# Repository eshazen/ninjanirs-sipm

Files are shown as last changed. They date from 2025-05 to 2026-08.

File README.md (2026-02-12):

# ninjanirs-sipm

Power supplies and electronics for SiPM-based optodes

Designs completed:

*  `KiCAD/lt3014-test` - test board with LT3014 voltage regulator
controlled by AD5270 digital pot, with INA201 current limiter
   * See [README](Testing/LT3014/README.md) for test details
* `KiCAD/sipm-hv-splitter` - candidate for in-system test
   * See [README](KiCAD/sipm-hv-splitter/README.md) for testing

Test logs:

* `Testing/LT3014` for the test board
* `Testing/sipm-splitter` for the splitter board

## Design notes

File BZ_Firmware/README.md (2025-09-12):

`20250827_SiPM_Test.zip`

The firmware for the purple test board is actually CircuitPython, so
it was very easy to modify. Attached, you just need to drag and drop
the .py files, and then the voltages of the 8 inputs should show up on
the serial port. If CircuitPython is not installed, I also included
the .uf2 file.

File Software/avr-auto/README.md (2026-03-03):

# avr-auto

Stand-alone bias voltage software.

* Set pull-up on PD0
* Turn off on-board LED
* Start boost converter with pot set to low voltage and output disabled
* Power up at low voltage and check voltage and current
* Power down
* Wait for low on PD0
* Power up at nominal voltage (pot=195, V=57.0V).  Check current

```
   Pot = 1023
   ADC 0 = low (10 or less)
   ADC 1 = 470  (33 volts or so)
```

LED code:
	On for 1s on power-up
	Off while waiting for start pulse
	Short blink at 1Hz during normal operation (bias on)
	fast continuous blink on error condition

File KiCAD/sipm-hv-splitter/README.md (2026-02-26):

# sipm-hv-splitter

## Description

This is a PCB intended to replace the "splitter" board, connecting
directly to a detector interface card with a very short ribbon.
It provides programmable, current-limited HV bias to 8 SiPMs along
with TIA readout of each SiPM.

The targent dimensions for the prototype are 2.5 x 1.3 inches.

The SiPM connectors are the "NIRX" standard .050" pitch 4-pin with
pinout as follows (top view of female header on this board):

| Function   | Number |   | Number | Function     |
|------------|--------|---|--------|--------------|
| V(BIAS)    | 2      |   | 1      | Signal       |
| Thermistor | 4      |   | 3      | GND (shield) |

The thermistor is optional and expected to be connected on only 1 of 8
SiPMs. 

The output connector to the readout adapter has the following pinout:

| Function | Number |   | Number | Function    |
|----------|--------|---|--------|-------------|
| V +12V   | 1      |   | 2      | V -20V      |
| GND      | 3      |   | 4      | Ch 7 signal |
| V +12V   | 5      |   | 6      | V -20V      |
| GND      | 7      |   | 8      | Ch 6 signal |
| V +12V   | 9      |   | 10     | V -20V      |
| GND      | 11     |   | 12     | Ch 6 signal |
| V +12V   | 13     |   | 14     | V -20V      |
| GND      | 15     |   | 16     | Ch 4 signal |
| V +12V   | 17     |   | 18     | V -20V      |
| GND      | 19     |   | 20     | Ch 3 signal |
| V +12V   | 21     |   | 22     | V -20V      |
| GND      | 23     |   | 24     | Ch 2 signal |
| V +12V   | 25     |   | 26     | V -20V      |
| GND      | 27     |   | 28     | Ch 1 signal |
| V +12V   | 29     |   | 30     | V -20V      |
| GND      | 31     |   | 32     | Ch 0 signal |
| COMM/RX  | 33     |   | 34     | COMM/RX     |

_NOTE:_ channel number order reversed to minimise crosstalk on the PCB.

`COMM/RX` is a logic signal (optionally containing UART prototcol
data) from the adapter card to the on-board MCU.  `COMM/TX` is an
optional half-duplex return path for bidirectional communication with
the adapter card.

## ECOs

* Cut track to SDO U5 pin 7 at chip.  Add 2.2k pull-up to 3.3V
on pin 7.
* Cut track to BOOST_ENA and wire to PD5 (pin 9) of U1.
* C39 wrong footprint on schematic/BOM (0201)

## Testing Log

### 2/26/26:

Thinking some more about the observed issues.  On the splitter the delta-v on
the LT3014 output is around 50mV, while on the test board with the MOSFET
load circuit it's more like 20mV.  50mv/57V * 1.2V = 1.1mV on the ADJ pin.
It seems not unlikely that ground bounce or capacitative coupling into the
ADJ pin could cause this.

Interesting... there is a C installed at C15 (soft start).  Try removing it.
Much better.

### 2/3/26:

Change feedback C on ch1 TIA from 1nf to 100pF.
<br>Oscillation gone!

Work plan after chat with BZ:

* Try various FB C's to make sure we're in a good range
* Change all FB C's on working board
* Test for measurable x-talk during 1.25ms pulse on neighboring channel
   * Shift in baseline
   * Change in Vbias
* Test with more SiPMs

<br>Change ch 2 FB to 470pF.  No oscillation.
<br>Change ch 1 FB back to 1000pF.  Yes oscillation (sanity check)
<br>Change ch 1-4 FB to 470pF.

### 2/2/26:

Power-up sequence:

    >p 170
	>vs 0
	>b 1

Should read 57V or so.  Note dummy load needed to avoid trip.

Testing S13360-3025PE.  3x3mm 25um pitch.  Vover = 5V, VBR 53+/-5
<br>Confirm that VBR is about 53.

   S13360-3025PE (gain 7e5)
   pot = 195.  V is 56V, 170uA+/-50uA
   100Hz pulse 100us wide 3.2V into red LED
   Output about 420mV.
   
Printing another box for a 2nd SiPM.

   S13360-3050PE (gain 1.7e6)
   Output about 3.95V
   
Gain should be about 2.5X higher.

__Oscillation:__ See 50MHz sine wave ~ 20mV pk-pk output of amp.
<br>With only open NIRX cable (60cm) we see a square-ish wave almost 100mV pk-pk.

The amp has a low-pass filter with ~10kHz cutoff.
<br>Try 100pF in parallel with the 1nF feedback cap.  If anything, worse.

### 1/22/26:

See below 8/7/25 for power hookups

Test board `OUT0` is pin 4 of ribbon, so SIG_0 which comes from pins 29-32 of Optodes header

Boost converter producing 73V but output always tripped.  Need dummy load?
<br>Make a optode cable with 100k.  Now it works!

The current readback seems wrong, though.  57/100k = 560uA
<br>The readout says 72.6uA

ADC is reading 31.  Sense resistor is 3.00 ohms.  So the raw current signal
should be 1.7mV across R9.  For the INA201 the gain is supposedly 50V/V
so 84mV for 560uA.  The expected ADC reading would be 26.  Observe 31-35
using raw `a 0` so maybe not so bad?

In `sipm_io.h` constant `NA_PER_ADC` is 2200.  Hmm.
Change to 20687.

### 9/30/25:

Testing board#2

* Power-up and flash OK.
* Boost output 73V
* VR range 31.2-60.8

* Change R17 to 2.7M to increase max voltage to 67V

Now the VR goes up to 65.2.

The current readback is jumping around from 8-20uA though.

Re-flash board#1 with avr-debug

Current readback similarly jumps around

### 9/17/25:

(all below board#1)

Finally have correct (hope) ribbon between test board and adapter.
Going to install firmware on the purple test board.

Currently it has:

```
hazen@hazen-botlab CIRCUITPY $ ls -l
total 6
-rw-r--r-- 1 hazen hazen  103 Dec 31  2019 boot_out.txt
-rw-r--r-- 1 hazen hazen 1608 Dec 18  2022 code.py
-rw-r--r-- 1 hazen hazen 2671 Dec 19  2022 DetAdapterTB.py
drwxr-xr-x 2 hazen hazen  512 Dec 31  2019 lib
```

(lib is empty).  Copying the following from BZ's ZIP:

```
-rw-rw-rw- 1 hazen hazen     889 Aug 28 00:51 code.py
-rw-rw-rw- 1 hazen hazen    8512 Aug 28 00:47 NN22DetectorAdapterTestBoard.py
-rw-rw-rw- 1 hazen hazen    3982 Oct 17  2024 TestFunctions.py
```

It works!  SiPM output voltage reported by python on the test board
varies with LED current.

### 9/12/25:

Working towards readout with BZ's red and purple boards.

TODO:

* Install R63, remove R62 on red board.  This disables the on-board LED and repurposes `A_COMM` as an
enable for the HV.  _Done_ (100 ohms for R63)
* Make firmware which powers up the HV and displays status
on the HV board LED.

### 9/11/25:

* Change R13 to 180k to up boost output to 75V.
* Change R17 to 2.7M to increase max voltage to 67V

Confirm with VOM we get 66.5V max output or so.

### 8/27/25:

Looking to use [test board](https://github.com/eshazen/ninjanirs-optode/tree/main/KiCAD/test-board) as a breakout.

```
  +6.5V  -  use for +12V power
  GND    -  ground
  -20V   -  use for -20V for TIA negative power
```

Solder wires to J1 pins 33 (comm TX) and 34 (comm RX).

### 8/20/25:

Load resistor of 66k on outputs.  Script `ramp_plot.py` makes
a nice set of V, I curvs vs DAC setting.

Ripple with scope probe ~ 20mV pk-pk.  100MHz always present,
20Hz (!) only when boost converter on.

Install parts for detector 0:

```
   R44, C47  (1k, 0.1uF) bias filter
   C23, C31 (0.1uF) bypass
   R28 (15k, TI)
   U13 (opa)
   R36 (15 ohms) output
   C39 (1n) feedback
```

### 8/4/25:

Issues with oscillation on output; seems like the LT3014.
Change C11 and C12 to 1uF 100V (vs 0.1uF).  Seems better.
Still some issues with startup.

Change R3 from 140k to 75k (double the overcurrent).
Now all seems good except for some ripple at max output.
Change R13 from 180k to 160k to up boost output to 65V.

All good so far.

### 7/29/25:

Add 2.2k pull-up on Digi Pot SDO.  It works!
<br>Move `BOOST_ENA` to PD5

Install U4, R17, R20 and C11, C12 as 0.1uF 100V.

### 7/28/25:

Started a new board, installed MCU and digi pot.

Found that ISP is unreliable here too.  Cut "SDO" track from digipot.
Now it seems to work reliably.  But Digi pot doesn't work.

Notice that the data sheet says that a pull-up is *required* on SDO
even if not used.

### 7/24/25:

Found a "feature" of the AVR SPI bus:  The pin called nSS (PB2)
must be driven high for the SPI bus to work.  We're using this
for BOOST_ENA so this is a bit of a problem.

More seriously, the ISP interface on the AVR seems to be dead.
This could be because we were using the ISP in 5V mode :(
<br>One can set 3.3V (host power) mode by removing the little yellow jumper
on the USBTinyISP.

May need to solder up a new board :( :(
<br>Start on board#2.  Install only 3.3V digital and MCU.
Programs fine.  Stopping for the weekend.

### 7/23/25:

Soldered 3.3V regulators, MCU and boost converter parts.
Soldered temporary FTDI serial thing on R1 site.

Boost converter works!  Outputting 61.3V, drawing 69mA on 12V.
Controlled as expected by `BOOST_ENA` output from MCU.

Install Digi pot.  Doesn't work :(  <br>
Verified SCK, MOSI, nSYNC all look OK. <br>
Nothing comes out MISO, POT stuck at 50%. <br>

Giving up for today

## Revision log

### 7/7/25:
Final checks

* Add LC filter on AVCC on MCU
* Add filter C on AREF
   * working on layout changes

### 7/3/25:  
First complete draft, posted to Basecamp

### Edits due from BZ on 7/1/25:

* Mis-wired RC filter on TIA input; should be on each SiPM bias line.
<br>_NOTE:_ the RC filter should be moved to the heirarchial block for
each channel for common layout? *DONE*
* Swap UART TX/RX *DONE*
* Use same symbol for all caps C2, C3 etc *DONE*
* Add filter on `THERM` *DONE*

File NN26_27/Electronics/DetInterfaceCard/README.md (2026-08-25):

## Detector card V03

Two variants:

| Designator | NN24-26        | NN27  | Notes                             |
|------------|----------------|-------|-----------------------------------|
| R71        | DNP            | 0 Ohm | New component / designator        |
| LF1        | BLM18AG601SN1D | DNP   | Ferrite 600 Ohm @ 100 MHz, 500 mA |

Additional components could be DNP’d in NN27 if desired, such as U13 and C104.

**2026-08-24**

Trying to order.  Two problem parts:

C89 etc.  10uF X5R 0402

D1-D2  SBR1A20T5-7  1A fast response diode.  A problem.

Possible sub:  SBR1U40LP-7 in DFN package about the same size.
Make this change in `develop` (KiCAD conversion).  Layout done.

BOM is a problem... the KiCAD import doesnt include MPN.

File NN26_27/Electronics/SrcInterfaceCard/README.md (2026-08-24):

# Source adapter V02

Two different possible assemblies here:

* NN22_VCCS_SrcAdapter02_s00_Gerber.zip -- Standard version
* NN22_VCCS_SrcAdapter02_s00_HiPower.zip -- High power version

The high power version has several BOM changes:

```
 Designator    NN24              NN26         Notes
 R9            10 Ohm            1 Ohm        Change in damping network
 R13           DNP               2.2 Ohm      Change in damping network
 C12           DNP               0.22 uF      Change in damping network
 R8            8.2 Ohm           1.5 Ohm      Current shunt for higher amps
 R30           28 kOhm           59 kOhm      Increase LED drive voltage for series cfg
 F1            0ZCH0035FF2G      0ZCH0110AF2E Increase fuse amps
 R2            10 kOhm           12 kOhm      Tune max amps slightly lower
```

Also the bottom silkscreen label has been changed to add the date 2026
and the notation "HIGH POWER".

There is an updated BOM downloaded from MacroFab.

As of today (8/6/26) the MacroFab design NN22_VCCS_SrcAdapter02
version 2 is the high power version.  Version 1 is the std one.

**2026-08-24** Ordered 20 pcs of the HP source adapter on Macrofab (#jr15eh3)

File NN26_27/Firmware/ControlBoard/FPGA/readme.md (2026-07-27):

For low-level Matlab functions or the old Matlab based NinjaGUI, which use the **USB** connection, use:  
`NN22Control00g5-ExtFifo-VCCS-VBoost-7000HC`

For use with **NinjaWeb**, running on the on-board Raspberry Pi Zero, which uses the **SPI** connection, use:  
`NN22Control00j-SPIctrl-Status-7000HC`

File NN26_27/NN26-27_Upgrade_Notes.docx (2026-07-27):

# NinjaNIRS 2026/27 Upgrade Notes

As of July 27, 2026

Github repo for all design files that have changed compared to the public version on OpenfNIRS: https://github.com/eshazen/ninjanirs-sipm/tree/main/NN26_27/

# NinjaNIRS 2026

NN26 is a planned upgrade of the two NN24 whole-head, high-density systems at BU with high-power source optodes, as designed and tested for the UG3 grant milestones.

## Source Optodes

NIRx is in the process of manufacturing high-power source optodes for us. Assembly instructions as well as the PCB design files for the small board inside each optode are in the Github repo.

## Source Splitter Boards

In testing we have used the NIRx source splitter PCBs and didn’t see any issues. It might still be worth checking the current handling capacities of the PCB traces.

The traces on Eric’s source splitter were designed with the higher currents in mind, but we have only manufactured a few of them.

## Source Interface Cards

The NN24 VCCS Source Interface cards from NN24 can also be used for NN26, however several components need to be changed, so it is probably more economical to order new sets of PCBs. Obviously regular NIRx source optodes should not be connected to these modified boards as the LEDs could easily be overdriven!

Here are the components that need to be changed:

Designator | NN24 | NN26 | Notes
R9 | 10 Ohm | 1 Ohm | Change in damping network
R13 | DNP | 2.2 Ohm | Change in damping network
C12 | DNP | 0.22 uF | Change in damping network
R8 | 8.2 Ohm | 1.5 Ohm | Current shunt for higher amps
R30 | 28 kOhm | 59 kOhm | Increase LED drive voltage for series cfg
F1 | 0ZCH0035FF2G | 0ZCH0110AF2E | Increase fuse amps
R2 | 10 kOhm | 12 kOhm | Tune max amps slightly lower

## Backplane

The NN24 backplane should be fine. Any backplane with “VCCS” in the designator should be compatible. Only the oldest (v1) backplanes are not compatible as they were designed for the first version source cards without current source.

## Control Card

Currently one NN24 system has a v2 control card, the other one has a v3 control card. Both are compatible with the high power optodes, though it would make sense to upgrade the system with the v2 card to v3 when working on it. V3 supports the voltage/current monitoring Sreekanth added to the NinjaWeb.

## System Case

The current case should be fine.

## Firmware / NinjaWeb GUI

It would be highly advisable to implement some additional safety features to prevent the average optical power of a single optode to exceed ANSI limits. This could currently happen if someone e.g. loads a wrong probe file for much smaller probe so that now the duty cycle of a single optode is much higher.
This safety could e.g. be implemented in the source card firmware, running separately on the second core of the MCU which is currently not used. Or a simpler version could be implemented in NinjaWEB, though this would not catch e.g. as stall in the FPGA.

In NinjaWEB, make sure that in NN24SystemClass.py the following is set:

self.v_src_boost = True

This will increase the source card supply voltage from 5.2V to 9.7V.

A similar setting is in the Matlab initStat() function: stat.v_src_boost = true;

# NinjaNIRS 2027

NN27 is a further planned upgrade of the two whole-head, high-density systems at BU with SiPM based high-detectivity optodes, as designed and tested for the UG3 grant milestones.

## Detector Optodes

Detector optodes can be manufactured by NIRx in exactly the same way as source optodes. PCB design files are in the Github repo.

## Detector Splitter Boards

Eric has designed splitter boards that contain the necessary bias voltage generator. A set of these will have to be ordered, maybe including minor revisions.

Protection of the user from the ~60V bias voltage should also be considered. Potting or conformal coating could be explored.

## Detector Interface Cards

The detector interface cards stay largely the same. The only change is to route 12V directly to the splitter board to power the bias generator. This can either be done by manually soldering a jumper wire on a current board, bypassing U13, or by manufacturing a new set of v3 cards with the following changes:

Designator | NN24-26 | NN27 | Notes
R71 | DNP | 0 Ohm | New component / designator
LF1 | BLM18AG601SN1D | DNP | Ferrite 600 Ohm @ 100 MHz, 500 mA

Additional components could be DNP’d in NN27 if desired, such as U13 and C104.

## Backplane

The existing backplanes are compatible.

## Control Card

Similar to the detector cards, 12V must be routed to the backplane to ultimately power the bias generators. The v3 Control Cards already have provisions for this. V1 and V2 cards are not compatible.

Here are the necessary changes on the v3 control card:

On the front side of the card, bridge pads 3 and 5 of connector footprint J901.

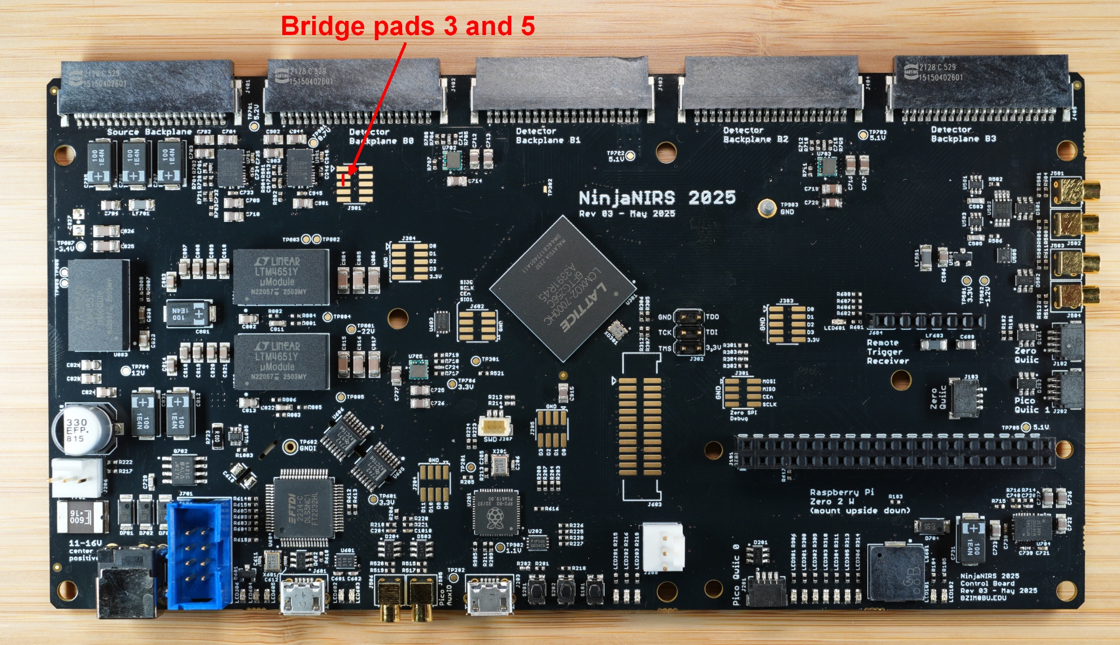
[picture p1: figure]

On the back side of the card, move the 0 Ohm resistor from R401 to R402, from R403 to R404, from R405 to R406, and from R407 to R408.

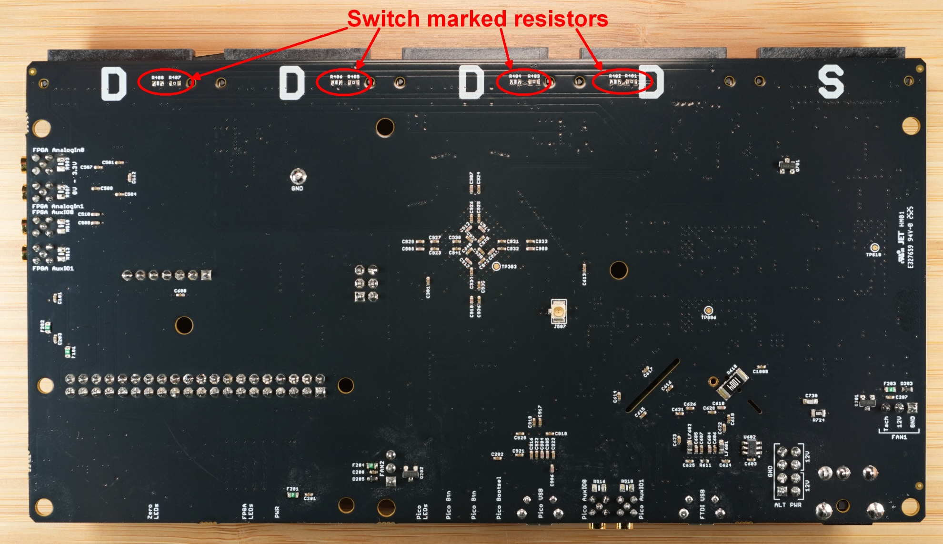
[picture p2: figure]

## System Case

The system case must be redesigned / enlarged to accommodate the larger detector splitter boards, and possibly to protect the user from the bias voltage.

## Firmware / NinjaWeb GUI

As a starting point, no firmware needs to be changed.

However, if control of bias voltage is necessary, it might be desirable to coordinate changes with the larger system, so communication between the splitter board and detector interface board has to be implemented, and then enable communication of this new data to NinjaWeb will also require changes to the FPGA firmware.

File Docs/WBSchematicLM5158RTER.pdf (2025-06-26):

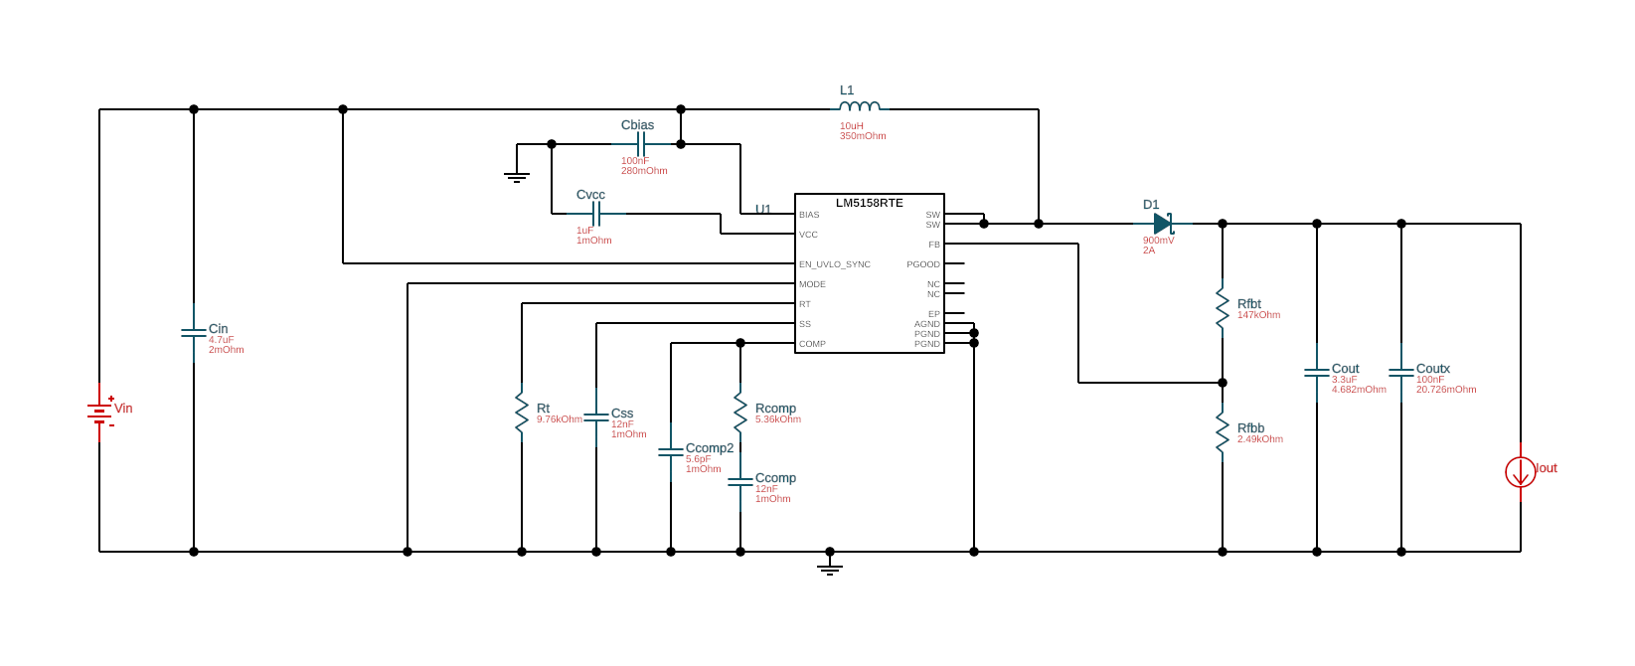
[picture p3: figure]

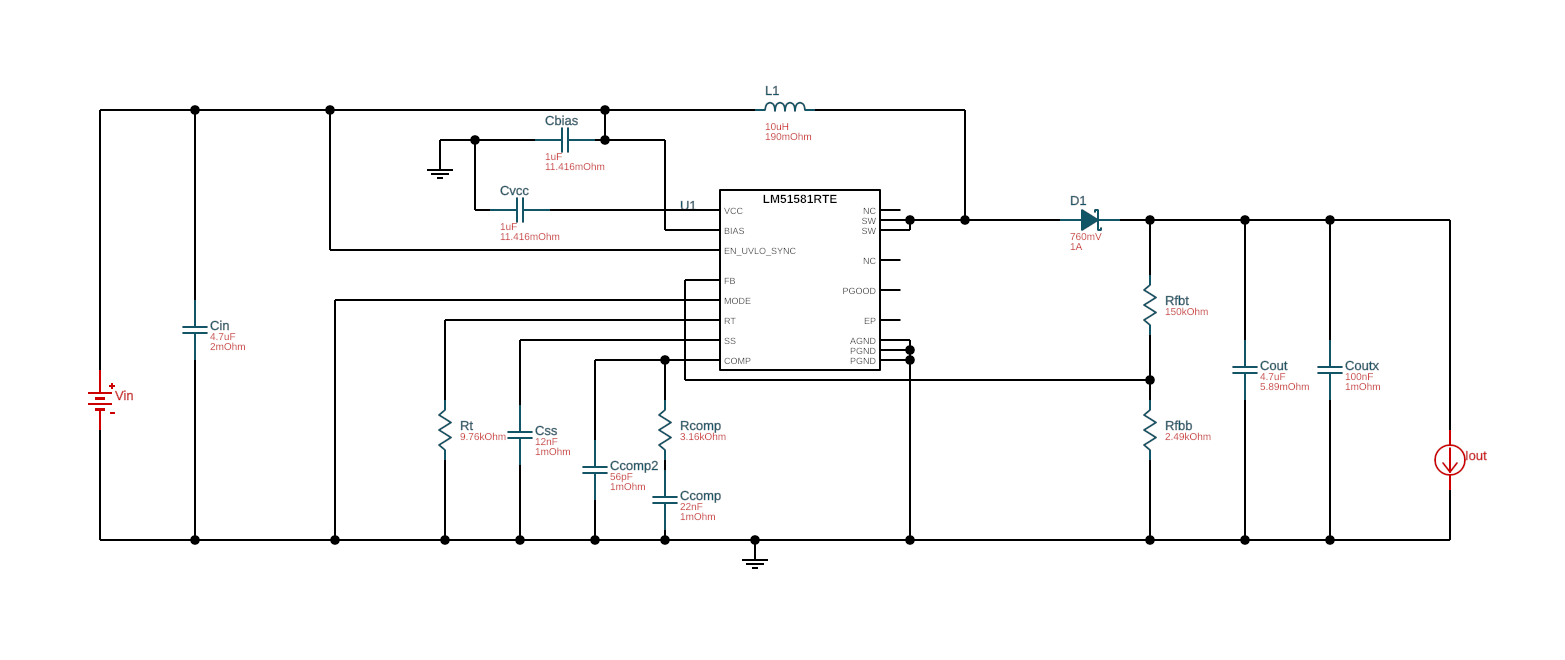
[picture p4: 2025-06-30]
Docs/WBSchematicLM51581RTER.png

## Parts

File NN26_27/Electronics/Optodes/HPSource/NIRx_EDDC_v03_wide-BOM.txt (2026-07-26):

LED1, LED2: Marubeni EDCC760D-1100
LED3, LED4: Marubeni EDCC850D-1100

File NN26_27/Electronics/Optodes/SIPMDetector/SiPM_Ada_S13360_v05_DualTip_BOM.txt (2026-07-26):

PD1, PD2: Hamamatsu S13360-3050PE
R1: NTCG163JF103FT1
TP1, TP2, TP3, TP4: DNP (wire solder pads)

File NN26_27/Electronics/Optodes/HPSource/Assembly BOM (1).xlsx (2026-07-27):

Type | No. | Description | Quantity per | Unit of Measure Code | Position
Item | ACLIP4 | POD Clip - 4 | 2 | PCS
Item | ACLIP8 | POD Clip - 8 | 1 | PCS
Item | NC000625 | Active SR2/DT2 optode cable Rev.04 (0.7M) | 8 | PCS
Item | NC000116 | Shrink Tube 1.6/0.5, 3:1, transp. (Optode Cable) | 0.152 | M
Item | NC000137 | Detector housing; double tip (DUAL CHIP SENSOR TIP) | 8 | PCS
Item | NC000192 | Optode cap blue | 8 | PCS
Item | NC000455 | Detector Box with cover for NSP2 (machined) | 1 | PCS
Item | NC000447 | SR2-POD-PCB | 1 | PCS

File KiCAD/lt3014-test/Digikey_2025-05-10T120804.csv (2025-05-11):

Index | Quantity | Part Number | Manufacturer Part Number | Description | Customer Reference | Available | Backorder | Unit Price | Extended Price USD
1 | 2 | 2648-SC0917-ND | SC0917 | RASPBERRY PI PICO H RP2040 | A1 | 2 | 0 | 5.00000 | 10.00
2 | 10 | 399-C0603C103M4REC7411CT-ND | C0603C103M4REC7411 | CAP CER 0603 10NF 16V X7R 20% | C6,C9 | 10 | 0 | 0.05400 | 0.54
3 | 10 | 3147-B19Y1USD-20C000113U1930CT-ND | B19Y1USD-20C000113U1930 | LED RED CLEAR 0603 SMD | D1,D2,D3,D4 | 10 | 0 | 0.09900 | 0.99
4 | 10 | SAM10844-ND | TSW-102-07-F-S | CONN HEADER VERT 2POS 2.54MM | J1,J2,J3 | 10 | 0 | 0.11000 | 1.10
5 | 10 | 609-3257-ND | 68000-208HLF | CONN HEADER VERT 8POS 2.54MM | J4 | 10 | 0 | 0.44900 | 4.49
6 | 10 | 609-3255-ND | 68000-204HLF | CONN HEADER VERT 4POS 2.54MM | J5 | 10 | 0 | 0.27000 | 2.70
7 | 10 | BSS138CT-ND | BSS138 | MOSFET N-CH 50V 220MA SOT23-3 | Q3,Q4,Q5 | 10 | 0 | 0.16100 | 1.61
8 | 10 | RMCF0603FT3R00CT-ND | RMCF0603FT3R00 | RES 3 OHM 1% 1/10W 0603 | R1 | 10 | 0 | 0.02400 | 0.24
9 | 10 | RMCF0603FT2M49CT-ND | RMCF0603FT2M49 | RES 2.49M OHM 1% 1/10W 0603 | R2 | 10 | 0 | 0.02400 | 0.24
10 | 10 | 13-RT0603BRD0750KLCT-ND | RT0603BRD0750KL | RES 50K OHM 0.1% 1/10W 0603 | R3 | 10 | 0 | 0.10800 | 1.08
11 | 10 | YAG1676CT-ND | RT0603BRD074K7L | RES SMD 4.7K OHM 0.1% 1/10W 0603 | R4 | 10 | 0 | 0.10000 | 1.00
12 | 20 | YAG1570CT-ND | RT0603BRD071K5L | RES SMD 1.5K OHM 0.1% 1/10W 0603 | R6,R8,R17,R18 | 20 | 0 | 0.10100 | 2.02
13 | 3 | LT3014ES5#TRPBFCT-ND | LT3014ES5#TRPBF | IC REG LIN POS ADJ 20MA TSOT23-5 | U1 | 3 | 0 | 6.07000 | 18.21
14 | 3 | 296-INA201AIDRCT-ND | INA201AIDR | IC CURRENT MONITOR 3.5% 8SOIC | U3 | 3 | 0 | 3.74000 | 11.22
15 | 3 | 505-AD5270BRMZ-50-ND | AD5270BRMZ-50 | IC DGT RHE 50KOHM 1024TAP 10MSOP | U4 | 3 | 0 | 6.75000 | 20.25
16 | 10 | 1276-1946-1-ND | CL10B105KP8NNNC | CAP CER 1UF 10V X7R 0603 | C4,C5,C7 | 10 | 0 | 0.00500 | 0.05
17 | 10 | 311-10.0KHRCT-ND | RC0603FR-0710KL | RES 10K OHM 1% 1/10W 0603 | R5,R10,R15 | 10 | 0 | 0.00900 | 0.09
18 | 10 | 311-100KHRCT-ND | RC0603FR-07100KL | RES 100K OHM 1% 1/10W 0603 | R7,R16 | 10 | 0 | 0.00900 | 0.09
19 | 10 | 311-100KHRCT-ND | RC0603FR-07100KL | RES 100K OHM 1% 1/10W 0603 | R9 | 10 | 0 | 0.00900 | 0.09
20 | 10 | 311-210KHRCT-ND | RC0603FR-07210KL | RES 210K OHM 1% 1/10W 0603 | R11 | 10 | 0 | 0.00900 | 0.09
21 | 10 | 311-140KHRCT-ND | RC0603FR-07140KL | RES 140K OHM 1% 1/10W 0603 | R12 | 10 | 0 | 0.00800 | 0.08
22 | 10 | 311-0.0GRCT-ND | RC0603JR-070RL | RES 0 OHM JUMPER 1/10W 0603 | R13,R14 | 10 | 0 | 0.01000 | 0.10

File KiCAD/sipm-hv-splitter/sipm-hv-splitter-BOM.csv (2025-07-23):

Build Qty: | 3
Reference | Qty | Value | MfgNo | CatNo | OrderQty
C1 | 1 | 4.7uF | CL10A475KO8NNNC | 1276-1784-1-ND | 3
C2,C3,C6,C48,C50,C52,C53 | 7 | 1.0uF | CL10B105KO8NNNC | 1276-1019-1-ND | 21
C4,C16,C17,C18,C19,C20,C21,C22,C23,C24,C25,C26,C27,C28,C29,C30,C31,C40,C41,C42,C43,C44,C45,C46,C47,C54,C55 | 27 | 0.1uF | CC0603KRX7R7BB104 | 311-1088-1-ND | 81
C5,C13 | 2 | 10nF | 06035C103MAZ2A | 478-KGF15AR71H103MTCT-ND | 6
C7 | 1 | 22nF | 0603B223K160CT | 1292-1415-1-ND | 3
C8 | 1 | 56pF | 600S560JT250XT4K | 478-600S560JT250XT4KCT-ND | 3
C9 | 1 | 4.7uF 100V | GRM31CC72A475KE11L | 490-18620-1-ND | 3
C10 | 1 | 0.1uF 100V | CL10B104KC8NNNC | 1276-6807-1-ND | 3
C11,C12,C14 | 3 | 1.0uF 100V | GRM188D72A105ME01W | 490-GRM188D72A105ME01WCT-ND | 9
C32,C33,C34,C35,C36,C37,C38,C39 | 8 | 1nF | CL03B102KOSVPNC | 1276-CL03B102KOSVPNCCT-ND | 24
C49,C51 | 2 | 2.2uF | TMK107ABJ225KA-T | 587-2909-1-ND | 6
D1 | 1 | MBR1H100SFT3G | MBR1H100SFT3G | MBR1H100SFT3GOSCT-ND | 3
D2,D3 | 2 | LED | B19Y1USD-20C000113U1930 | 3147-B19Y1USD-20C000113U1930CT-ND | 6
J1 | 1 | Conn_02x18_Odd_Even | SFMC-118-02-S-D | SFMC-118-02-S-D-ND | 3
J2 | 1 | Conn_02x17_Odd_Even | SHF-117-01-L-D-SM | SAM9921-ND | 3
J3 | 1 | ISP | BC065-06-A-L-D | 2073-BC065-06-A-L-D-ND | 3
L1 | 1 | 10uH | 744025100 | 732-2617-1-ND | 3
L2 | 1 | 10uH | MLZ1608N100LT000 | 445-6755-1-ND | 3
Q1,Q2,Q3 | 3 | BSS138 | BSS138 | BSS138CT-ND | 9
R1,R37,R38,R39,R40,R41,R42,R43,R44 | 9 | 1k | RMCF0603FT1K00 | RMCF0603FT1K00CT-ND | 27
R2 | 1 | 210k | RC0603FR-07210KL | 311-210KHRCT-ND | 3
R3 | 1 | 140k | RC0603FR-07140KL | 311-140KHRCT-ND | 3
R4 | 1 | 100k | RC0603FR-07100KL | 311-100KHRCT-ND | 3
R5,R6,R16,R46 | 4 | 10.0k | CRCW0603100KFKEA,RC0603FR-0710KL | 311-10.0KHRCT-ND | 12
R7 | 1 | 100k | CRCW0603100KFKEA | 541-100KHCT-ND | 3
R8,R10 | 2 | 100 | ERJ-3EKF1000V | P100HCT-ND | 6
R9 | 1 | 3.00 1% | MFCR1206F3R00QHR | 4506-MFCR1206F3R00QHRCT-ND | 3
R11 | 1 | 4.7k | RT0603BRD074K7L | YAG1676CT-ND | 3
R12 | 1 | 3.16k | CRCW06033K16FKEAC | 541-5389-1-ND | 3
R13 | 1 | 150k | ERJ-3EKF1503V | P150KHCT-ND | 3
R14 | 1 | 2.49k | CRCW06032K49FKEAC | 541-4044-1-ND | 3
R15,R47 | 2 | 1.5k | RT0603BRD071K5L | YAG1570CT-ND | 6
R17 | 1 | 2.50M 1% | RMCF0603FT2M49 | RMCF0603FT2M49CT-ND | 3
R18 | 1 | 510k 1% | RMCF0603FT510K | RMCF0603FT510KCT-ND | 3
R19 | 1 | 24.0k 1% | RMCF0603FT24K0 | RMCF0603FT24K0CT-ND | 3
R20 | 1 | 50.0k 1% | RT0603BRD0750KL | 13-RT0603BRD0750KLCT-ND | 3
R21,R22,R23,R24,R25,R26,R27,R28 | 8 | 15k | CRG0603F15K | A121558CT-ND | 24
R29,R30,R31,R32,R33,R34,R35,R36 | 8 | 15 | RC0603FR-0715RL | 311-15.0HRCT-ND | 24
R45 | 1 | 4.7k | ERJ-3EKF4701V | P4.70KHCT-ND | 3
U1 | 1 | ATmega328-M | ATMEGA328P-MU | ATMEGA328P-MU-ND | 3
U2 | 1 | INA201 | INA201AIDR | 296-INA201AIDRCT-ND | 3
U3 | 1 | LM51581 | LM51581RTER | 296-LM51581RTERCT-ND | 3
U4 | 1 | LT3014xS5 | LT3014ES5#TRPBF | LT3014ES5#TRPBFCT-ND | 3
U5 | 1 | AD5270 | AD5270BRMZ-50 | 505-AD5270BRMZ-50-ND | 3
U6,U7,U8,U9,U10,U11,U12,U13 | 8 | OPA810xDCK | OPA810IDCKR | 296-OPA810IDCKRCT-ND | 24
U14,U16 | 2 | TPS7A25 | TPS7A2533DRVR | 296-TPS7A2533DRVRCT-ND | 6

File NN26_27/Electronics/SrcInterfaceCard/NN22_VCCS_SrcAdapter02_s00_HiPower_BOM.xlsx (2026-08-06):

Designator | Value | Footprint | Populate | MPN | Manufacturer | MPN | Manufacturer
C1 | 0.1u | 0402-CAP | 1 | GRM155R71H104KE14D | Murata
C10 | 0.1u | 0402-CAP | 1 | GRM155R71H104KE14D | Murata
C11 | 10n | 0402-CAP | 1 | CL05B103KB5NNNC | Samsung
C12 | DNP | 0603-CAP | 1 | GCM188R71H224KA64D | Murata
C13 | 100p | 0402-CAP | 1 | CL05C101JB5NNNC | Samsung
C14 | 100p | 0402-CAP | 1 | CL05C101JB5NNNC | Samsung
C15 | 100p | 0402-CAP | 1 | CL05C101JB5NNNC | Samsung
C16 | 100p | 0402-CAP | 1 | CL05C101JB5NNNC | Samsung
C17 | 0.1u | 0402-CAP | 1 | GRM155R71H104KE14D | Murata
C18 | 27p | 0402-CAP | 1 | GCM1555C1H270JA16D | Murata
C19 | 27p | 0402-CAP | 1 | GCM1555C1H270JA16D | Murata
C2 | 0.1u | 0402-CAP | 1 | GRM155R71H104KE14D | Murata
C20 | 150u | 2917-CAP | 1 | TCJY157M016R0050E | KYOCERA AVX
C21 | 0.1u | 0402-CAP | 1 | GRM155R71H104KE14D | Murata
C22 | 10u | 0603-CAP | 1 | GRM188R6YA106MA73D | Murata
C23 | 0.1u | 0402-CAP | 1 | GRM155R71H104KE14D | Murata
C24 | 10u | 0603-CAP | 1 | GRM188R6YA106MA73D | Murata
C25 | 0.1u | 0402-CAP | 1 | GRM155R71H104KE14D | Murata
C26 | 4.7u | 0402-CAP | 1 | CL05A475MP5NRNC | Samsung
C27 | 4.7u | 0402-CAP | 1 | CL05A475MP5NRNC | Samsung
C28 | 4.7u | 0402-CAP | 1 | CL05A475MP5NRNC | Samsung
C29 | 4.7u | 0402-CAP | 1 | CL05A475MP5NRNC | Samsung
C3 | 0.1u | 0402-CAP | 1 | GRM155R71H104KE14D | Murata
C30 | 0.1u | 0402-CAP | 1 | GRM155R71H104KE14D | Murata
C31 | 4.7u | 0402-CAP | 1 | CL05A475MP5NRNC | Samsung
C32 | DNP | 0402-CAP | 0
C33 | 0.1u | 0402-CAP | 1 | GRM155R71H104KE14D | Murata
C34 | 0.1u | 0402-CAP | 1 | GRM155R71H104KE14D | Murata
C35 | 4.7u | 0402-CAP | 1 | CL05A475MP5NRNC | Samsung
C36 | 0.1u | 0402-CAP | 1 | GRM155R71H104KE14D | Murata
C37 | 4.7u | 0402-CAP | 1 | CL05A475MP5NRNC | Samsung
C38 | 0.1u | 0402-CAP | 1 | GRM155R71H104KE14D | Murata
C39 | 0.1u | 0402-CAP | 1 | GRM155R71H104KE14D | Murata
C4 | 10n | 0402-CAP | 1 | CL05B103KB5NNNC | Samsung
C40 | 4.7u | 0402-CAP | 1 | CL05A475MP5NRNC | Samsung
C41 | 0.1u | 0402-CAP | 1 | GRM155R71H104KE14D | Murata
C42 | 0.1u | 0402-CAP | 1 | GRM155R71H104KE14D | Murata
C43 | 0.1u | 0402-CAP | 1 | GRM155R71H104KE14D | Murata
C44 | 10u | 0603-CAP | 1 | GRM188R6YA106MA73D | Murata
C45 | 10u | 0603-CAP | 1 | GRM188R6YA106MA73D | Murata
C46 | 10u | 0603-CAP | 1 | GRM188R6YA106MA73D | Murata
C5 | 0.1u | 0402-CAP | 1 | GRM155R71H104KE14D | Murata
C6 | 100p | 0402-CAP | 1 | CL05C101JB5NNNC | Samsung
C7 | 0.1u | 0402-CAP | 1 | GRM155R71H104KE14D | Murata
C8 | 0.1u | 0402-CAP | 1 | GRM155R71H104KE14D | Murata
C9 | 100p | 0402-CAP | 1 | CL05C101JB5NNNC | Samsung
D1 | BAV70W | SOT323 | 1 | BAV70WT1G | onsemi
D10 | BAV70W | SOT323 | 1 | BAV70WT1G | onsemi
D11 | BAV70W | SOT323 | 1 | BAV70WT1G | onsemi
D2 | BAV70W | SOT323 | 1 | BAV70WT1G | onsemi
D3 | BAV70W | SOT323 | 1 | BAV70WT1G | onsemi
D4 | BAV70W | SOT323 | 1 | BAV70WT1G | onsemi
D5 | BAV70W | SOT323 | 1 | BAV70WT1G | onsemi
D6 | BAV70W | SOT323 | 1 | BAV70WT1G | onsemi
D7 | BAV70W | SOT323 | 1 | BAV70WT1G | onsemi
D8 | BAV70W | SOT323 | 1 | BAV70WT1G | onsemi
D9 | BAV70W | SOT323 | 1 | BAV70WT1G | onsemi
F1 | 0ZCH0035FF2G | 1210-FUSE | 1 | 0ZCH0110AF2E | Bel Fuse
FID1 | FIDUCIALUFIDUCIAL | MICRO-FIDUCIAL | 0
FID2 | FIDUCIALUFIDUCIAL | MICRO-FIDUCIAL | 0
FID3 | FIDUCIALUFIDUCIAL | MICRO-FIDUCIAL | 0
FID4 | FIDUCIALUFIDUCIAL | MICRO-FIDUCIAL | 0
FID5 | FIDUCIALUFIDUCIAL | MICRO-FIDUCIAL | 0
FID6 | FIDUCIALUFIDUCIAL | MICRO-FIDUCIAL | 0
FID7 | FIDUCIALUFIDUCIAL | MICRO-FIDUCIAL | 0
FID8 | FIDUCIALUFIDUCIAL | MICRO-FIDUCIAL | 0
J1 | M04X2_0.050_SMD_NO_CREAM | M04X2_0.050_SMD_NO_CREAM | 0
J2 | M13X2_0.050_SHF | M13X2_0.050_SHF | 1 | 3220-26-0300-00 | CNC Tech | 3220-26-0300-00-TR | CNC Tech
J3 | M04X2_0.050_SMD_NO_CREAM | M04X2_0.050_SMD_NO_CREAM | 0
J4 | U.FL | U.FL | 1 | 1909763-1 | TE Connectivity
J5 | M20X2_HARFLEX_M | M20X2_HARFLEX_M | 1 | 15150402601000 | HARTING Elektronik
J6 | M03X1_JST_SH_RA | M03X1_JST_SH_SM_RA | 1 | SM03B-SRSS-TB | JST
J7 | USB-MICRO | USB-MICRO | 1 | 10118194-0001LF | Amphenol Communications Solutions
LED1 |  | LED-0603 | 1 | LTST-C191KRKT | Lite-On
LED2 |  | LED-0603 | 1 | LTST-C191KGKT | Lite-On
Q1 | MOSFET-DUAL-N-UDFN8 | UDFN8 | 1 | SSM6N67NU,LF | Toshiba
Q10 | MOSFET-DUAL-N-UDFN8 | UDFN8 | 1 | SSM6N67NU,LF | Toshiba
Q2 | MOSFET-DUAL-N-UDFN8 | UDFN8 | 1 | SSM6N67NU,LF | Toshiba
Q3 | MOSFET-DUAL-N-UDFN8 | UDFN8 | 1 | SSM6N67NU,LF | Toshiba
Q4 | MOSFET-DUAL-N-UDFN8 | UDFN8 | 1 | SSM6N67NU,LF | Toshiba
Q5 | MOSFET-DUAL-N-UDFN8 | UDFN8 | 1 | SSM6N67NU,LF | Toshiba
Q6 | MOSFET-DUAL-N-UDFN8 | UDFN8 | 1 | SSM6N67NU,LF | Toshiba
Q7 | MOSFET-DUAL-N-UDFN8 | UDFN8 | 1 | SSM6N67NU,LF | Toshiba
Q8 | MOSFET-DUAL-N-UDFN8 | UDFN8 | 1 | SSM6N67NU,LF | Toshiba
Q9 | MOSFET-DUAL-N-UDFN8 | UDFN8 | 1 | SSM6N67NU,LF | Toshiba
R1 | 0 | 1206 | 1 | RC1206JR-070RL | Yageo
R10 | 100 | 0402-RES | 1 | RC0402FR-07100RL | Yageo
R11 | 1 | 0603-RES | 1 | RC0603FR-071RL | Yageo
R12 | 150 | 0603-RES | 1 | RC0603FR-07150RL | Yageo
R13 | DNP | 0603-RES | 1 | CRCW06032R20FKEA | Vishay
R14 | 1.2k | 0402-RES | 1 | RC0402FR-071K2L | Yageo
R15 | 1.2k | 0402-RES | 1 | RC0402FR-071K2L | Yageo
R16 | 10k | 0402-RES | 1 | RC0402FR-1310KL | Yageo
R17 | 28k | 0402-RES | 1 | RC0402FR-0728KL | Yageo
R18 | 28k | 0402-RES | 1 | RC0402FR-0728KL | Yageo
R19 | 10k | 0402-RES | 1 | RC0402FR-1310KL | Yageo
R2 | 10k | 0402-RES | 1 | RC0402FR-0712KL | Yageo Group
R20 | 1.2k | 0402-RES | 1 | RC0402FR-071K2L | Yageo
R21 | 100k | 0402-RES | 1 | RC0402FR-07100KL | Yageo
R22 | 100k | 0402-RES | 1 | RC0402FR-07100KL | Yageo
R23 | 1.2k | 0402-RES | 1 | RC0402FR-071K2L | Yageo
R24 | 27 | 0402-RES | 1 | RC0402FR-0727RL | Yageo
R25 | 27 | 0402-RES | 1 | RC0402FR-0727RL | Yageo
R26 | 100k | 0402-RES | 1 | RC0402FR-07100KL | Yageo
R27 | 10k | 0402-RES | 1 | RC0402FR-1310KL | Yageo
R28 | 10k | 0402-RES | 1 | RC0402FR-1310KL | Yageo
R29 | 24k | 0402-RES | 1 | RC0402FR-0724KL | Yageo
R3 | 24k | 0402-RES | 1 | RC0402FR-0724KL | Yageo
R30 | 28k | 0402-RES | 1 | CRCW040259K0FKED | Vishay
R31 | 27 | 0402-RES | 1 | RC0402FR-0727RL | Yageo
R32 | 10k | 0402-RES | 1 | RC0402FR-1310KL | Yageo
R33 | 27 | 0402-RES | 1 | RC0402FR-0727RL | Yageo
R34 | 27 | 0402-RES | 1 | RC0402FR-0727RL | Yageo
R4 | 10k | 0402-RES | 1 | RC0402FR-1310KL | Yageo
R5 | 10k | 0402-RES | 1 | RC0402FR-1310KL | Yageo
R6 | 100 | 0402-RES | 1 | RC0402FR-07100RL | Yageo
R7 | 1.2k | 0402-RES | 1 | RC0402FR-071K2L | Yageo
R8 | 8.2 | R2512 | 1 | RC2512FK-071R5L | Yageo Group
R9 | 10 | 0603-RES | 1 | RC0603FR-071RL | Yageo Group
S1 | SWITCH-MOMENTARY-2SMD-3 | TACTILE_SWITCH_SMD-3 | 1 | KMR231NGLFS | C&K Components
TP1 | TESTPOINT_ROUND | TESTPAD_ROUND | 0
TP10 | TESTPOINT_ROUND | TESTPAD_ROUND | 0
TP11 | TESTPOINT_ROUND | TESTPAD_ROUND | 0
TP12 | TESTPOINTPADSMALL | TESTPAD_SMALL | 0
TP13 | TESTPOINT1X01 | 1X01 | 0
TP14 | TESTPOINTPADSMALL | TESTPAD_SMALL | 0
TP15 | TESTPOINT_ROUND | TESTPAD_ROUND | 0
TP2 | TESTPOINT_ROUND | TESTPAD_ROUND | 0
TP3 | TESTPOINT_ROUND | TESTPAD_ROUND | 0
TP4 | TESTPOINT_ROUND | TESTPAD_ROUND | 0
TP5 | TESTPOINTPADSMALL | TESTPAD_SMALL | 0
TP6 | TESTPOINTPADSMALL | TESTPAD_SMALL | 0
TP7 | TESTPOINT_ROUND | TESTPAD_ROUND | 0
TP8 | TESTPOINT_ROUND | TESTPAD_ROUND | 0
TP9 | TESTPOINT_ROUND | TESTPAD_ROUND | 0
U1 | 74HC238_TSSOP | TSSOP16 | 1 | SN74HCS238PWR | Texas Instruments
U10 | LDL212_DFN6_3X3 | DFN6_3X3MM | 1 | LDL212PUR | STMicroelectronics
U2 | 74HC238_TSSOP | TSSOP16 | 1 | SN74HCS238PWR | Texas Instruments
U3 | AD5683R_MSOP | MSOP10 | 1 | AD5683RARMZ | Analog Devices
U4 | OPA392_SOT23 | SOT23-5 | 1 | OPA392DBVR | Texas Instruments
U5 | RP2040 | QFN-56_EP | 1 | SC0914(7) | Raspberry Pi
U6 | W25Q_USON | USON8L-2X3MM | 1 | W25Q16JVUXIQ TR | Winbond
U7 | ADP7182_WSON | WSON6 | 1 | ADP7182ACPZN-R7 | Analog Devices
U8 | MCP1755_DFN | DFN8_2X3MM | 1 | MCP1755-3302E/MC | Microchip
U9 | LDL212_DFN6_3X3 | DFN6_3X3MM | 1 | LDL212PUR | STMicroelectronics
X1 | CRYSTAL-3.2-2.5 | CRYSTAL-3.2-2.5 | 1 | 403I35D12M00000 | CTS Components

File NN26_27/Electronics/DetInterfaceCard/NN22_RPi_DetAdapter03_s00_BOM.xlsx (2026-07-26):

Designator | Value | Footprint | Populate | MPN | Manufacturer
C1 | 330p | 0402-CAP | 1 | GRM1555C1H331JA01D | Murata
C10 | 0.1u | 0402-CAP | 1 | GRM155R71H104KE14D | Murata
C100 | 0.1u | 0402-CAP | 1 | GRM155R71H104KE14D | Murata
C101 | 0.1u | 0402-CAP | 1 | GRM155R71H104KE14D | Murata
C102 | 0.1u | 0402-CAP | 1 | GRM155R71H104KE14D | Murata
C103 | 0.1u | 0402-CAP | 1 | GRM155R71H104KE14D | Murata
C104 | 10u | 0603-CAP | 1 | GRM188R6YA106MA73D | Murata
C105 | 4.7u | 0402-CAP | 1 | CL05A475MP5NRNC | Samsung
C106 | 10u | 0603-CAP | 1 | GRM188R6YA106MA73D | Murata
C107 | 4.7u | 0402-CAP | 1 | CL05A475MP5NRNC | Samsung
C108 | 10u | 0603-CAP | 1 | GRM188R6YA106MA73D | Murata
C109 | 10u | 0603-CAP | 1 | GRM188R6YA106MA73D | Murata
C11 | 330p | 0402-CAP | 1 | GRM1555C1H331JA01D | Murata
C110 | 33n | 0402-CAP | 1 | GCM155R71E333KA55D | Murata
C111 | 4.7u | 0402-CAP | 1 | CL05A475MP5NRNC | Samsung
C112 | 4.7u | 0402-CAP | 1 | CL05A475MP5NRNC | Samsung
C113 | 4.7u | 0402-CAP | 1 | CL05A475MP5NRNC | Samsung
C12 | 1u | 0402-CAP | 1 | CL05A105KP5NNNC | Samsung
C13 | 0.1u | 0402-CAP | 1 | GRM155R71H104KE14D | Murata
C14 | 1u | 0402-CAP | 1 | CL05A105KP5NNNC | Samsung
C15 | 1n | 0402-CAP | 1 | GRM1555C1H102JA01D | Murata
C16 | 1n | 0402-CAP | 1 | GRM1555C1H102JA01D | Murata
C17 | 1n | 0402-CAP | 1 | GRM1555C1H102JA01D | Murata
C18 | 330p | 0402-CAP | 1 | GRM1555C1H331JA01D | Murata
C19 | 0.1u | 0402-CAP | 1 | GRM155R71H104KE14D | Murata
C2 | 1n | 0402-CAP | 1 | GRM1555C1H102JA01D | Murata
C20 | 0.1u | 0402-CAP | 1 | GRM155R71H104KE14D | Murata
C21 | 0.1u | 0402-CAP | 1 | GRM155R71H104KE14D | Murata
C22 | 330p | 0402-CAP | 1 | GRM1555C1H331JA01D | Murata
C23 | 1n | 0402-CAP | 1 | GRM1555C1H102JA01D | Murata
C24 | 1n | 0402-CAP | 1 | GRM1555C1H102JA01D | Murata
C25 | 1n | 0402-CAP | 1 | GRM1555C1H102JA01D | Murata
C26 | 330p | 0402-CAP | 1 | GRM1555C1H331JA01D | Murata
C27 | 1u | 0402-CAP | 1 | CL05A105KP5NNNC | Samsung
C28 | 1u | 0402-CAP | 1 | CL05A105KP5NNNC | Samsung
C29 | 0.1u | 0402-CAP | 1 | GRM155R71H104KE14D | Murata
C3 | 1n | 0402-CAP | 1 | GRM1555C1H102JA01D | Murata
C30 | 0.1u | 0402-CAP | 1 | GRM155R71H104KE14D | Murata
C31 | 0.1u | 0402-CAP | 1 | GRM155R71H104KE14D | Murata
C32 | 330p | 0402-CAP | 1 | GRM1555C1H331JA01D | Murata
C33 | 1u | 0402-CAP | 1 | CL05A105KP5NNNC | Samsung
C34 | 0.1u | 0402-CAP | 1 | GRM155R71H104KE14D | Murata
C35 | 1u | 0402-CAP | 1 | CL05A105KP5NNNC | Samsung
C36 | 1n | 0402-CAP | 1 | GRM1555C1H102JA01D | Murata
C37 | 1n | 0402-CAP | 1 | GRM1555C1H102JA01D | Murata
C38 | 1n | 0402-CAP | 1 | GRM1555C1H102JA01D | Murata
C39 | 330p | 0402-CAP | 1 | GRM1555C1H331JA01D | Murata
C4 | 1n | 0402-CAP | 1 | GRM1555C1H102JA01D | Murata
C40 | 0.1u | 0402-CAP | 1 | GRM155R71H104KE14D | Murata
C41 | 0.1u | 0402-CAP | 1 | GRM155R71H104KE14D | Murata
C42 | 0.1u | 0402-CAP | 1 | GRM155R71H104KE14D | Murata
C43 | 330p | 0402-CAP | 1 | GRM1555C1H331JA01D | Murata
C44 | 1n | 0402-CAP | 1 | GRM1555C1H102JA01D | Murata
C45 | 1n | 0402-CAP | 1 | GRM1555C1H102JA01D | Murata
C46 | 1n | 0402-CAP | 1 | GRM1555C1H102JA01D | Murata
C47 | 330p | 0402-CAP | 1 | GRM1555C1H331JA01D | Murata
C48 | 1u | 0402-CAP | 1 | CL05A105KP5NNNC | Samsung
C49 | 1u | 0402-CAP | 1 | CL05A105KP5NNNC | Samsung
C5 | 330p | 0402-CAP | 1 | GRM1555C1H331JA01D | Murata
C50 | 0.1u | 0402-CAP | 1 | GRM155R71H104KE14D | Murata
C51 | 0.1u | 0402-CAP | 1 | GRM155R71H104KE14D | Murata
C52 | 0.1u | 0402-CAP | 1 | GRM155R71H104KE14D | Murata
C53 | 330p | 0402-CAP | 1 | GRM1555C1H331JA01D | Murata
C54 | 1u | 0402-CAP | 1 | CL05A105KP5NNNC | Samsung
C55 | 0.1u | 0402-CAP | 1 | GRM155R71H104KE14D | Murata
C56 | 1u | 0402-CAP | 1 | CL05A105KP5NNNC | Samsung
C57 | 1n | 0402-CAP | 1 | GRM1555C1H102JA01D | Murata
C58 | 1n | 0402-CAP | 1 | GRM1555C1H102JA01D | Murata
C59 | 1n | 0402-CAP | 1 | GRM1555C1H102JA01D | Murata
C6 | 1u | 0402-CAP | 1 | CL05A105KP5NNNC | Samsung
C60 | 330p | 0402-CAP | 1 | GRM1555C1H331JA01D | Murata
C61 | 0.1u | 0402-CAP | 1 | GRM155R71H104KE14D | Murata
C62 | 0.1u | 0402-CAP | 1 | GRM155R71H104KE14D | Murata
C63 | 0.1u | 0402-CAP | 1 | GRM155R71H104KE14D | Murata
C64 | 330p | 0402-CAP | 1 | GRM1555C1H331JA01D | Murata
C65 | 1n | 0402-CAP | 1 | GRM1555C1H102JA01D | Murata
C66 | 1n | 0402-CAP | 1 | GRM1555C1H102JA01D | Murata
C67 | 1n | 0402-CAP | 1 | GRM1555C1H102JA01D | Murata
C68 | 330p | 0402-CAP | 1 | GRM1555C1H331JA01D | Murata
C69 | 1u | 0402-CAP | 1 | CL05A105KP5NNNC | Samsung
C7 | 1u | 0402-CAP | 1 | CL05A105KP5NNNC | Samsung
C70 | 1u | 0402-CAP | 1 | CL05A105KP5NNNC | Samsung
C71 | 0.1u | 0402-CAP | 1 | GRM155R71H104KE14D | Murata
C72 | 0.1u | 0402-CAP | 1 | GRM155R71H104KE14D | Murata
C73 | 0.1u | 0402-CAP | 1 | GRM155R71H104KE14D | Murata
C74 | 330p | 0402-CAP | 1 | GRM1555C1H331JA01D | Murata
C75 | 1u | 0402-CAP | 1 | CL05A105KP5NNNC | Samsung
C76 | 0.1u | 0402-CAP | 1 | GRM155R71H104KE14D | Murata
C77 | 1u | 0402-CAP | 1 | CL05A105KP5NNNC | Samsung
C78 | 1n | 0402-CAP | 1 | GRM1555C1H102JA01D | Murata
C79 | 1n | 0402-CAP | 1 | GRM1555C1H102JA01D | Murata
C8 | 0.1u | 0402-CAP | 1 | GRM155R71H104KE14D | Murata
C80 | 1n | 0402-CAP | 1 | GRM1555C1H102JA01D | Murata
C81 | 330p | 0402-CAP | 1 | GRM1555C1H331JA01D | Murata
C82 | 0.1u | 0402-CAP | 1 | GRM155R71H104KE14D | Murata
C83 | 0.1u | 0402-CAP | 1 | GRM155R71H104KE14D | Murata
C84 | 0.1u | 0402-CAP | 1 | GRM155R71H104KE14D | Murata
C85 | 0.1u | 0402-CAP | 1 | GRM155R71H104KE14D | Murata
C86 | 27p | 0402-CAP | 1 | GCM1555C1H270JA16D | Murata
C87 | 27p | 0402-CAP | 1 | GCM1555C1H270JA16D | Murata
C88 | 10u | 0603-CAP | 1 | GRM188R6YA106MA73D | Murata
C89 | 4.7u | 0402-CAP | 1 | CL05A475MP5NRNC | Samsung
C9 | 0.1u | 0402-CAP | 1 | GRM155R71H104KE14D | Murata
C90 | 4.7u | 0402-CAP | 1 | CL05A475MP5NRNC | Samsung
C91 | 4.7u | 0402-CAP | 1 | CL05A475MP5NRNC | Samsung
C92 | 4.7u | 0402-CAP | 1 | CL05A475MP5NRNC | Samsung
C93 | 4.7u | 0402-CAP | 1 | CL05A475MP5NRNC | Samsung
C94 | 4.7u | 0402-CAP | 1 | CL05A475MP5NRNC | Samsung
C95 | 4.7u | 0402-CAP | 1 | CL05A475MP5NRNC | Samsung
C96 | 0.1u | 0402-CAP | 1 | GRM155R71H104KE14D | Murata
C97 | 0.1u | 0402-CAP | 1 | GRM155R71H104KE14D | Murata
C98 | 0.1u | 0402-CAP | 1 | GRM155R71H104KE14D | Murata
C99 | 0.1u | 0402-CAP | 1 | GRM155R71H104KE14D | Murata
D1 | SBR1A20T5 | SOD523 | 1 | SBR1A20T5-7 | Diodes Inc.
D2 | SBR1A20T5 | SOD523 | 1 | SBR1A20T5-7 | Diodes Inc.
FID1 | FIDUCIALUFIDUCIAL | MICRO-FIDUCIAL | 0
FID2 | FIDUCIALUFIDUCIAL | MICRO-FIDUCIAL | 0
FID3 | FIDUCIALUFIDUCIAL | MICRO-FIDUCIAL | 0
FID4 | FIDUCIALUFIDUCIAL | MICRO-FIDUCIAL | 0
FID5 | FIDUCIALUFIDUCIAL | MICRO-FIDUCIAL | 0
FID6 | FIDUCIALUFIDUCIAL | MICRO-FIDUCIAL | 0
FID7 | FIDUCIALUFIDUCIAL | MICRO-FIDUCIAL | 0
FID8 | FIDUCIALUFIDUCIAL | MICRO-FIDUCIAL | 0
J1 | M17X2 | M17X2_0.050_SHF | 1 | SHF-117-01-L-D-SM | Samtec
J2 | M05X2_SMD_0.050_NOCREAM | M05X2_0.050_SMD_NO_CREAM | 0
J3 | M03X1_0.050_SMD_NO_CREAM | M03X1_0.050_SMD_NO_CREAM | 0
J4 | USB-MICRO | USB-MICRO | 1 | 10118194-0001LF | Amphenol Communications Solutions
J5 | M20X2_HARFLEX_M | M20X2_HARFLEX_M | 1 | 15150402601000 | HARTING Elektronik
LED1 |  | LED-0603 | 1 | LTST-C191KRKT | Lite-On
LF1 | FERRITE0603 | 0603-FER | 1 | BLM18AG601SN1D | Murata
LF2 | FERRITE0603 | 0603-FER | 1 | BLM18AG601SN1D | Murata
R1 | 18k | 0402-RES | 1 | RR0510P-183-D | Susumu
R10 | 18k | 0402-RES | 1 | RR0510P-183-D | Susumu
R11 | 2.2k | 0402-RES | 1 | RR0510P-222-D | Susumu
R12 | 33 | 0402-RES | 1 | CRCW040233R0FKEDC | Vishay
R13 | 18k | 0402-RES | 1 | RR0510P-183-D | Susumu
R14 | 18k | 0402-RES | 1 | RR0510P-183-D | Susumu
R15 | 18k | 0402-RES | 1 | RR0510P-183-D | Susumu
R16 | 2.2k | 0402-RES | 1 | RR0510P-222-D | Susumu
R17 | 33 | 0402-RES | 1 | CRCW040233R0FKEDC | Vishay
R18 | 18k | 0402-RES | 1 | RR0510P-183-D | Susumu
R19 | 2.2k | 0402-RES | 1 | RR0510P-222-D | Susumu
R2 | 2.2k | 0402-RES | 1 | RR0510P-222-D | Susumu
R20 | 33 | 0402-RES | 1 | CRCW040233R0FKEDC | Vishay
R21 | 18k | 0402-RES | 1 | RR0510P-183-D | Susumu
R22 | 2.2k | 0402-RES | 1 | RR0510P-222-D | Susumu
R23 | 33 | 0402-RES | 1 | CRCW040233R0FKEDC | Vishay
R24 | 18k | 0402-RES | 1 | RR0510P-183-D | Susumu
R25 | 2.2k | 0402-RES | 1 | RR0510P-222-D | Susumu
R26 | 33 | 0402-RES | 1 | CRCW040233R0FKEDC | Vishay
R27 | 18k | 0402-RES | 1 | RR0510P-183-D | Susumu
R28 | 18k | 0402-RES | 1 | RR0510P-183-D | Susumu
R29 | 18k | 0402-RES | 1 | RR0510P-183-D | Susumu
R3 | 33 | 0402-RES | 1 | CRCW040233R0FKEDC | Vishay
R30 | 2.2k | 0402-RES | 1 | RR0510P-222-D | Susumu
R31 | 33 | 0402-RES | 1 | CRCW040233R0FKEDC | Vishay
R32 | 18k | 0402-RES | 1 | RR0510P-183-D | Susumu
R33 | 2.2k | 0402-RES | 1 | RR0510P-222-D | Susumu
R34 | 33 | 0402-RES | 1 | CRCW040233R0FKEDC | Vishay
R35 | 18k | 0402-RES | 1 | RR0510P-183-D | Susumu
R36 | 2.2k | 0402-RES | 1 | RR0510P-222-D | Susumu
R37 | 33 | 0402-RES | 1 | CRCW040233R0FKEDC | Vishay
R38 | 18k | 0402-RES | 1 | RR0510P-183-D | Susumu
R39 | 2.2k | 0402-RES | 1 | RR0510P-222-D | Susumu
R4 | 18k | 0402-RES | 1 | RR0510P-183-D | Susumu
R40 | 33 | 0402-RES | 1 | CRCW040233R0FKEDC | Vishay
R41 | 18k | 0402-RES | 1 | RR0510P-183-D | Susumu
R42 | 18k | 0402-RES | 1 | RR0510P-183-D | Susumu
R43 | 18k | 0402-RES | 1 | RR0510P-183-D | Susumu
R44 | 2.2k | 0402-RES | 1 | RR0510P-222-D | Susumu
R45 | 33 | 0402-RES | 1 | CRCW040233R0FKEDC | Vishay
R46 | 18k | 0402-RES | 1 | RR0510P-183-D | Susumu
R47 | 2.2k | 0402-RES | 1 | RR0510P-222-D | Susumu
R48 | 33 | 0402-RES | 1 | CRCW040233R0FKEDC | Vishay
R49 | 18k | 0402-RES | 1 | RR0510P-183-D | Susumu
R5 | 2.2k | 0402-RES | 1 | RR0510P-222-D | Susumu
R50 | 2.2k | 0402-RES | 1 | RR0510P-222-D | Susumu
R51 | 33 | 0402-RES | 1 | CRCW040233R0FKEDC | Vishay
R52 | 18k | 0402-RES | 1 | RR0510P-183-D | Susumu
R53 | 2.2k | 0402-RES | 1 | RR0510P-222-D | Susumu
R54 | 33 | 0402-RES | 1 | CRCW040233R0FKEDC | Vishay
R55 | 18k | 0402-RES | 1 | RR0510P-183-D | Susumu
R56 | 18k | 0402-RES | 1 | RR0510P-183-D | Susumu
R57 | 1.2k | 0402-RES | 1 | RC0402FR-071K2L | Yageo
R58 | 100k | 0402-RES | 1 | RC0402FR-07100KL | Yageo
R59 | 100k | 0402-RES | 1 | RC0402FR-07100KL | Yageo
R6 | 33 | 0402-RES | 1 | CRCW040233R0FKEDC | Vishay
R60 | 27 | 0402-RES | 1 | RC0402FR-0727RL | Yageo
R61 | 27 | 0402-RES | 1 | RC0402FR-0727RL | Yageo
R62 | 1.2k | 0402-RES | 1 | RC0402FR-071K2L | Yageo
R63 | DNP | 0402-RES | 0
R64 | 1.2k | 0402-RES | 1 | RC0402FR-071K2L | Yageo
R65 | 33 | 0402-RES | 1 | CRCW040233R0FKEDC | Vishay
R66 | 30k | 0402-RES | 1 | RC0402FR-0730KL | Yageo
R67 | 100k | 0402-RES | 1 | RC0402FR-07100KL | Yageo
R68 | 10k | 0402-RES | 1 | RC0402FR-1310KL | Yageo
R69 | 154k | 0402-RES | 1 | RC0402FR-07154KL | Yageo
R7 | 18k | 0402-RES | 1 | RR0510P-183-D | Susumu
R70 | 10k | 0402-RES | 1 | RC0402FR-1310KL | Yageo
R71 | DNP | 0402-RES | 0
R8 | 2.2k | 0402-RES | 1 | RR0510P-222-D | Susumu
R9 | 33 | 0402-RES | 1 | CRCW040233R0FKEDC | Vishay
S1 | SWITCH-MOMENTARY-2SMD-3 | TACTILE_SWITCH_SMD-3 | 1 | KMR231NGLFS | C&K Components
TP1 | TESTPOINT_ROUND | TESTPAD_ROUND | 0
TP11 | TESTPOINT_ROUND | TESTPAD_ROUND | 0
TP12 | TESTPOINT_ROUND | TESTPAD_ROUND | 0
TP13 | TESTPOINT_ROUND | TESTPAD_ROUND | 0
TP15 | TESTPOINT_ROUND | TESTPAD_ROUND | 0
TP16 | TESTPOINT_ROUND | TESTPAD_ROUND | 0
TP17 | TESTPOINT_ROUND | TESTPAD_ROUND | 0
TP18 | TESTPOINT_ROUND | TESTPAD_ROUND | 0
TP19 | TESTPOINT_ROUND | TESTPAD_ROUND | 0
TP2 | TESTPOINT_ROUND | TESTPAD_ROUND | 0
TP20 | TESTPOINT1X01 | 1X01 | 0
TP21 | TESTPOINTPADSMALL | TESTPAD_SMALL | 0
TP22 | TESTPOINT_ROUND | TESTPAD_ROUND | 0
TP3 | TESTPOINT_ROUND | TESTPAD_ROUND | 0
TP4 | TESTPOINT_ROUND | TESTPAD_ROUND | 0
TP5 | TESTPOINT_ROUND | TESTPAD_ROUND | 0
TP6 | TESTPOINT_ROUND | TESTPAD_ROUND | 0
TP7 | TESTPOINT_ROUND | TESTPAD_ROUND | 0
TP8 | TESTPOINT_ROUND | TESTPAD_ROUND | 0
TP9 | TESTPOINT_ROUND | TESTPAD_ROUND | 0
U1 | AD7380 | LFCSP16 | 1 | AD7380BCPZ-RL7 | Analog Devices
U10 | RP2040 | QFN-56_EP | 1 | SC0914(7) | Raspberry Pi
U11 | MCP1755_DFN | DFN8_2X3MM | 1 | MCP1755-3302E/MC | Microchip
U12 | MCP1755_DFN | DFN8_2X3MM | 1 | MCP1755-3302E/MC | Microchip
U13 | ADP7142_WSON | WSON6 | 1 | ADP7142ACPZN5.0-R7 | Analog Devices
U14 | ADP7182_WSON | WSON6 | 1 | ADP7182ACPZN-R7 | Analog Devices
U15 | ADP7182_WSON | WSON6 | 1 | ADP7182ACPZN-R7 | Analog Devices
U2 | ADA4940-2 | LFCSP24 | 1 | ADA4940-2ACPZ-R7 | Analog Devices
U3 | AD7380 | LFCSP16 | 1 | AD7380BCPZ-RL7 | Analog Devices
U4 | ADA4940-2 | LFCSP24 | 1 | ADA4940-2ACPZ-R7 | Analog Devices
U5 | AD7380 | LFCSP16 | 1 | AD7380BCPZ-RL7 | Analog Devices
U6 | ADA4940-2 | LFCSP24 | 1 | ADA4940-2ACPZ-R7 | Analog Devices
U7 | AD7380 | LFCSP16 | 1 | AD7380BCPZ-RL7 | Analog Devices
U8 | ADA4940-2 | LFCSP24 | 1 | ADA4940-2ACPZ-R7 | Analog Devices
U9 | W25Q_USON | USON8L-2X3MM | 1 | W25Q16JVUXIQ TR | Winbond
X1 | CRYSTAL-3.2-2.5 | CRYSTAL-3.2-2.5 | 1 | 403I35D12M00000 | CTS Components

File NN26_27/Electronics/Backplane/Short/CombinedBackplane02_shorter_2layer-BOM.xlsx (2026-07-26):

CombinedBackplane02_short_2layer |  |  | bzim@bu.edu
Designator | Qty | MPN | Manufacturer | Value | Device | Package
J111, J112, J305, J306 | 4 | DNP |  | M04X2_0.050_SMD_NO_CREAM | M04X2_0.050_SMD_NO_CREAM | M04X2_0.050_SMD_NO_CREAM
J104, J204, J304, J404 | 4 | 1377302 | Phoenix Contact | M20X2_HARFLEX_M | M20X2_HARFLEX_M | M20X2_HARFLEX_M
J101, J102, J201, J202, J301, J302, J401, J402 | 8 | M55-6064042R | Harwin | M20X2_STR_MPTH | M20X2_STR_MPTH | M20X2_HARFLEX_F_STR_MPTH
TP107, TP407 | 2 | DNP |  | TESTPOINT1X01 | TESTPOINT1X01 | 1X01
TP101, TP102, TP103, TP104, TP105, TP106, TP201, TP202, TP301, TP302, TP303, TP304, TP305, TP306, TP401, TP402, TP403, TP404, TP405, TP406 | 20 | DNP |  | TESTPOINT_ROUND | TESTPOINT_ROUND | TESTPAD_ROUND

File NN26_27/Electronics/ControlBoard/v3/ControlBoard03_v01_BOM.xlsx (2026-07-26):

Designator | Value | Footprint | Populate | MPN | Manufacturer | MPN | Manufacturer
C1009 | 0.1u | 0402-CAP | 1 | GRM155R71H104KE14D | Murata
C101 | 0.1u | 0402-CAP | 1 | GRM155R71H104KE14D | Murata
C1010 | 0.1u | 0402-CAP | 1 | GRM155R71H104KE14D | Murata
C201 | 0.1u | 0402-CAP | 1 | GRM155R71H104KE14D | Murata
C202 | 0.1u | 0402-CAP | 1 | GRM155R71H104KE14D | Murata
C203 | 0.1u | 0402-CAP | 1 | GRM155R71H104KE14D | Murata
C204 | 0.1u | 0402-CAP | 1 | GRM155R71H104KE14D | Murata
C205 | 27p | 0402-CAP | 1 | GCM1555C1H270JA16D | Murata
C206 | 27p | 0402-CAP | 1 | GCM1555C1H270JA16D | Murata
C207 | 0.1u | 0402-CAP | 1 | GRM155R71H104KE14D | Murata
C208 | 0.1u | 0402-CAP | 1 | GRM155R71H104KE14D | Murata
C301 | 0.1u | 0402-CAP | 1 | GRM155R71H104KE14D | Murata
C501 | 0.1u | 0402-CAP | 1 | GRM155R71H104KE14D | Murata
C502 | 4.7u | 0402-CAP | 1 | CL05A475MP5NRNC | Samsung Electro-Mechanics
C503 | 10n | 0603-CAP | 1 | GRM1885C1H103JA01D | Murata
C504 | 0.1u | 0402-CAP | 1 | GRM155R71H104KE14D | Murata
C505 | 10n | 0603-CAP | 1 | GRM1885C1H103JA01D | Murata
C506 | 22u | 0805-CAP | 1 | CL21A226MAYNNNE | Samsung Electro-Mechanics
C507 | 0.1u | 0402-CAP | 1 | GRM155R71H104KE14D | Murata
C508 | 0.1u | 0402-CAP | 1 | GRM155R71H104KE14D | Murata
C509 | 4.7u | 0402-CAP | 1 | CL05A475MP5NRNC | Samsung Electro-Mechanics
C510 | 4.7u | 0402-CAP | 1 | CL05A475MP5NRNC | Samsung Electro-Mechanics
C601 | 4.7u | 0402-CAP | 1 | CL05A475MP5NRNC | Samsung Electro-Mechanics
C602 | 4.7u | 0402-CAP | 1 | CL05A475MP5NRNC | Samsung Electro-Mechanics
C603 | 0.1u | 0402-CAP | 1 | GRM155R71H104KE14D | Murata
C604 | 4.7u | 0402-CAP | 1 | CL05A475MP5NRNC | Samsung Electro-Mechanics
C605 | 4.7u | 0402-CAP | 1 | CL05A475MP5NRNC | Samsung Electro-Mechanics
C606 | 0.1u | 0402-CAP | 1 | GRM155R71H104KE14D | Murata
C607 | 0.1u | 0402-CAP | 1 | GRM155R71H104KE14D | Murata
C608 | 0.1u | 0402-CAP | 1 | GRM155R71H104KE14D | Murata
C609 | 22u | 0805-CAP | 1 | CL21A226MAYNNNE | Samsung Electro-Mechanics
C610 | 4.7u | 0402-CAP | 1 | CL05A475MP5NRNC | Samsung Electro-Mechanics
C611 | 27p | 0402-CAP | 1 | GCM1555C1H270JA16D | Murata
C612 | 27p | 0402-CAP | 1 | GCM1555C1H270JA16D | Murata
C613 | 0.1u | 0402-CAP | 1 | GRM155R71H104KE14D | Murata
C614 | 0.1u | 0402-CAP | 1 | GRM155R71H104KE14D | Murata
C615 | 0.1u | 0402-CAP | 1 | GRM155R71H104KE14D | Murata
C616 | 0.1u | 0402-CAP | 1 | GRM155R71H104KE14D | Murata
C617 | 0.1u | 0402-CAP | 1 | GRM155R71H104KE14D | Murata
C618 | DNP | 1210 | 0
C619 | 0.1u | 0402-CAP | 1 | GRM155R71H104KE14D | Murata
C620 | 0.1u | 0402-CAP | 1 | GRM155R71H104KE14D | Murata
C621 | 0.1u | 0402-CAP | 1 | GRM155R71H104KE14D | Murata
C622 | 0.1u | 0402-CAP | 1 | GRM155R71H104KE14D | Murata
C623 | 0.1u | 0402-CAP | 1 | GRM155R71H104KE14D | Murata
C624 | 0.1u | 0402-CAP | 1 | GRM155R71H104KE14D | Murata
C625 | 0.1u | 0402-CAP | 1 | GRM155R71H104KE14D | Murata
C626 | 0.1u | 0402-CAP | 1 | GRM155R71H104KE14D | Murata
C701 | 39p | 0402-CAP | 1 | GCM1555C1H390JA16D | Murata
C702 | 22u | 0805-CAP | 1 | CL21A226MAYNNNE | Samsung Electro-Mechanics
C703 | 22u | 0805-CAP | 1 | CL21A226MAYNNNE | Samsung Electro-Mechanics
C704 | 22u | 0805-CAP | 1 | CL21A226MAYNNNE | Samsung Electro-Mechanics
C705 | 100u/25V | 2917-CAP | 1 | TCJD107M025R0055 | KYOCERA AVX | 25TQC100MD3 | Panasonic
C706 | 22u | 0805-CAP | 1 | CL21A226MAYNNNE | Samsung Electro-Mechanics
C707 | 100u/25V | 2917-CAP | 1 | TCJD107M025R0055 | KYOCERA AVX | 25TQC100MD3 | Panasonic
C708 | 100u/25V | 2917-CAP | 1 | TCJD107M025R0055 | KYOCERA AVX | 25TQC100MD3 | Panasonic
C709 | 22u | 0805-CAP | 1 | CL21A226MAYNNNE | Samsung Electro-Mechanics
C710 | 22u | 0805-CAP | 1 | CL21A226MAYNNNE | Samsung Electro-Mechanics
C711 | 39p | 0402-CAP | 1 | GCM1555C1H390JA16D | Murata
C712 | 22u | 0805-CAP | 1 | CL21A226MAYNNNE | Samsung Electro-Mechanics
C713 | 22u | 0805-CAP | 1 | CL21A226MAYNNNE | Samsung Electro-Mechanics
C714 | 22u | 0805-CAP | 1 | CL21A226MAYNNNE | Samsung Electro-Mechanics
C715 | 39p | 0402-CAP | 1 | GCM1555C1H390JA16D | Murata
C716 | 22u | 0805-CAP | 1 | CL21A226MAYNNNE | Samsung Electro-Mechanics
C717 | 22u | 0805-CAP | 1 | CL21A226MAYNNNE | Samsung Electro-Mechanics
C718 | 330u/25V | CAP-SMD-POL-8X10 | 1 | EEE-FP1E331AP | Panasonic
C719 | 22u | 0805-CAP | 1 | CL21A226MAYNNNE | Samsung Electro-Mechanics
C720 | 39p | 0402-CAP | 1 | GCM1555C1H390JA16D | Murata
C721 | 0.1u | 0402-CAP | 1 | GRM155R71H104KE14D | Murata
C722 | 22u | 0805-CAP | 1 | CL21A226MAYNNNE | Samsung Electro-Mechanics
C723 | 22u | 0805-CAP | 1 | CL21A226MAYNNNE | Samsung Electro-Mechanics
C724 | 39p | 0402-CAP | 1 | GCM1555C1H390JA16D | Murata
C725 | 22u | 0805-CAP | 1 | CL21A226MAYNNNE | Samsung Electro-Mechanics
C726 | 22u | 0805-CAP | 1 | CL21A226MAYNNNE | Samsung Electro-Mechanics
C727 | 22u | 0805-CAP | 1 | CL21A226MAYNNNE | Samsung Electro-Mechanics
C728 | 22u | 0805-CAP | 1 | CL21A226MAYNNNE | Samsung Electro-Mechanics
C729 | 10n | 0603-CAP | 1 | GRM1885C1H103JA01D | Murata
C730 | 1n | 0603-CAP | 1 | GRM1885C1H102JA01D | Murata
C731 | 100u/25V | 2917-CAP | 1 | TCJD107M025R0055 | KYOCERA AVX | 25TQC100MD3 | Panasonic
C732 | 0.1u | 0402-CAP | 1 | GRM155R71H104KE14D | Murata
C733 | 0.1u | 0402-CAP | 1 | GRM155R71H104KE14D | Murata
C734 | DNP | 0402-CAP | 0
C735 | 0.1u | 0402-CAP | 1 | GRM155R71H104KE14D | Murata
C736 | 22u | 0805-CAP | 1 | CL21A226MAYNNNE | Samsung Electro-Mechanics
C737 | 22u | 0805-CAP | 1 | CL21A226MAYNNNE | Samsung Electro-Mechanics
C738 | 0.1u | 0402-CAP | 1 | GRM155R71H104KE14D | Murata
C739 | DNP | 0402-CAP | 0
C740 | 0.1u | 0402-CAP | 1 | GRM155R71H104KE14D | Murata
C801 | 100u/25V | 2917-CAP | 1 | TCJD107M025R0055 | KYOCERA AVX | 25TQC100MD3 | Panasonic
C802 | 4.7u | 0805-CAP | 1 | CL21A475KBQNNNE | Samsung Electro-Mechanics
C803 | 4.7u | 0805-CAP | 1 | CL21A475KBQNNNE | Samsung Electro-Mechanics
C804 | 10u | 1206 | 1 | CL31A106MBHNNNE | Samsung Electro-Mechanics
C805 | 10u | 1206 | 1 | CL31A106MBHNNNE | Samsung Electro-Mechanics
C806 | 10u | 1206 | 1 | CL31A106MBHNNNE | Samsung Electro-Mechanics
C807 | 4.7u | 0805-CAP | 1 | CL21A475KBQNNNE | Samsung Electro-Mechanics
C808 | 4.7u | 0805-CAP | 1 | CL21A475KBQNNNE | Samsung Electro-Mechanics
C809 | 4.7u | 0805-CAP | 1 | CL21A475KBQNNNE | Samsung Electro-Mechanics
C810 | 4.7u | 0805-CAP | 1 | CL21A475KBQNNNE | Samsung Electro-Mechanics
C811 | 1u | 0603-CAP | 1 | CL10A105KB8NNNC | Samsung Electro-Mechanics
C812 | 100u/25V | 2917-CAP | 1 | TCJD107M025R0055 | KYOCERA AVX | 25TQC100MD3 | Panasonic
C813 | 4.7u | 0805-CAP | 1 | CL21A475KBQNNNE | Samsung Electro-Mechanics
C814 | 4.7u | 0805-CAP | 1 | CL21A475KBQNNNE | Samsung Electro-Mechanics
C815 | 10u | 1206 | 1 | CL31A106MBHNNNE | Samsung Electro-Mechanics
C816 | 10u | 1206 | 1 | CL31A106MBHNNNE | Samsung Electro-Mechanics
C817 | 10u | 1206 | 1 | CL31A106MBHNNNE | Samsung Electro-Mechanics
C818 | 4.7u | 0805-CAP | 1 | CL21A475KBQNNNE | Samsung Electro-Mechanics
C819 | 4.7u | 0805-CAP | 1 | CL21A475KBQNNNE | Samsung Electro-Mechanics
C820 | 4.7u | 0805-CAP | 1 | CL21A475KBQNNNE | Samsung Electro-Mechanics
C821 | 4.7u | 0805-CAP | 1 | CL21A475KBQNNNE | Samsung Electro-Mechanics
C822 | 1u | 0603-CAP | 1 | CL10A105KB8NNNC | Samsung Electro-Mechanics
C823 | 4.7u | 0805-CAP | 1 | CL21A475KBQNNNE | Samsung Electro-Mechanics
C824 | 4.7u | 0805-CAP | 1 | CL21A475KBQNNNE | Samsung Electro-Mechanics
C825 | 100u | 1206 | 1 | CL31A107MQHNNNE | Samsung Electro-Mechanics
C826 | 100u | 1206 | 1 | CL31A107MQHNNNE | Samsung Electro-Mechanics
C827 | DNP | 1206 | 0
C828 | 4.7u | 0805-CAP | 1 | CL21A475KBQNNNE | Samsung Electro-Mechanics
C829 | 4.7u | 0805-CAP | 1 | CL21A475KBQNNNE | Samsung Electro-Mechanics
C830 | 1u | 0603-CAP | 1 | CL10A105KB8NNNC | Samsung Electro-Mechanics
C831 | 100u/25V | 2917-CAP | 1 | TCJD107M025R0055 | KYOCERA AVX | 25TQC100MD3 | Panasonic
C901 | 22u | 0805-CAP | 1 | CL21A226MAYNNNE | Samsung Electro-Mechanics
C902 | 22u | 0805-CAP | 1 | CL21A226MAYNNNE | Samsung Electro-Mechanics
C903 | 22u | 0805-CAP | 1 | CL21A226MAYNNNE | Samsung Electro-Mechanics
C904 | 4.7u | 0402-CAP | 1 | CL05A475MP5NRNC | Samsung Electro-Mechanics
C905 | 4.7u | 0402-CAP | 1 | CL05A475MP5NRNC | Samsung Electro-Mechanics
C906 | 4.7u | 0402-CAP | 1 | CL05A475MP5NRNC | Samsung Electro-Mechanics
C907 | 4.7u | 0402-CAP | 1 | CL05A475MP5NRNC | Samsung Electro-Mechanics
C908 | 4.7u | 0402-CAP | 1 | CL05A475MP5NRNC | Samsung Electro-Mechanics
C909 | 4.7u | 0402-CAP | 1 | CL05A475MP5NRNC | Samsung Electro-Mechanics
C910 | 4.7u | 0402-CAP | 1 | CL05A475MP5NRNC | Samsung Electro-Mechanics
C911 | 4.7u | 0402-CAP | 1 | CL05A475MP5NRNC | Samsung Electro-Mechanics
C912 | 4.7u | 0402-CAP | 1 | CL05A475MP5NRNC | Samsung Electro-Mechanics
C913 | 4.7u | 0402-CAP | 1 | CL05A475MP5NRNC | Samsung Electro-Mechanics
C914 | 4.7u | 0402-CAP | 1 | CL05A475MP5NRNC | Samsung Electro-Mechanics
C915 | 22u | 0805-CAP | 1 | CL21A226MAYNNNE | Samsung Electro-Mechanics
C916 | 0.1u | 0402-CAP | 1 | GRM155R71H104KE14D | Murata
C917 | 0.1u | 0402-CAP | 1 | GRM155R71H104KE14D | Murata
C918 | 0.1u | 0402-CAP | 1 | GRM155R71H104KE14D | Murata
C919 | 0.1u | 0402-CAP | 1 | GRM155R71H104KE14D | Murata
C920 | 0.1u | 0402-CAP | 1 | GRM155R71H104KE14D | Murata
C921 | 0.1u | 0402-CAP | 1 | GRM155R71H104KE14D | Murata
C922 | 0.1u | 0402-CAP | 1 | GRM155R71H104KE14D | Murata
C923 | 0.1u | 0402-CAP | 1 | GRM155R71H104KE14D | Murata
C924 | 0.1u | 0402-CAP | 1 | GRM155R71H104KE14D | Murata
C925 | 0.1u | 0402-CAP | 1 | GRM155R71H104KE14D | Murata
C926 | 0.1u | 0402-CAP | 1 | GRM155R71H104KE14D | Murata
C927 | 0.1u | 0402-CAP | 1 | GRM155R71H104KE14D | Murata
C928 | 0.1u | 0402-CAP | 1 | GRM155R71H104KE14D | Murata
C929 | 0.1u | 0402-CAP | 1 | GRM155R71H104KE14D | Murata
C930 | 0.1u | 0402-CAP | 1 | GRM155R71H104KE14D | Murata
C931 | 0.1u | 0402-CAP | 1 | GRM155R71H104KE14D | Murata
C932 | 0.1u | 0402-CAP | 1 | GRM155R71H104KE14D | Murata
C933 | 0.1u | 0402-CAP | 1 | GRM155R71H104KE14D | Murata
C934 | 0.1u | 0402-CAP | 1 | GRM155R71H104KE14D | Murata
C935 | 0.1u | 0402-CAP | 1 | GRM155R71H104KE14D | Murata
C936 | 0.1u | 0402-CAP | 1 | GRM155R71H104KE14D | Murata
C937 | 0.1u | 0402-CAP | 1 | GRM155R71H104KE14D | Murata
C938 | 0.1u | 0402-CAP | 1 | GRM155R71H104KE14D | Murata
C939 | 0.1u | 0402-CAP | 1 | GRM155R71H104KE14D | Murata
C940 | 0.1u | 0402-CAP | 1 | GRM155R71H104KE14D | Murata
C941 | 0.1u | 0402-CAP | 1 | GRM155R71H104KE14D | Murata
C942 | 0.1u | 0402-CAP | 1 | GRM155R71H104KE14D | Murata
C943 | 39p | 0402-CAP | 1 | GCM1555C1H390JA16D | Murata
C944 | 22u | 0805-CAP | 1 | CL21A226MAYNNNE | Samsung Electro-Mechanics
C945 | 0.1u | 0402-CAP | 1 | GRM155R71H104KE14D | Murata
C946 | DNP | 0402-CAP | 0
C947 | 0.1u | 0402-CAP | 1 | GRM155R71H104KE14D | Murata
C948 | 0.1u | 0402-CAP | 1 | GRM155R71H104KE14D | Murata
D101 | D1213A-02SO | SOT23-6 | 1 | D1213A-02SO-7 | Diodes Inc.
D201 | D1213A-02SO | SOT23-6 | 1 | D1213A-02SO-7 | Diodes Inc.
D202 | D1213A-02SO | SOT23-6 | 1 | D1213A-02SO-7 | Diodes Inc.
D203 |  | SOD523 | 1 | SBR1A20T5-7 | Diodes Inc.
D204 | D1213A-02SO | SOT23-6 | 1 | D1213A-02SO-7 | Diodes Inc.
D205 |  | SOD523 | 1 | SBR1A20T5-7 | Diodes Inc.
D501 | D1213A-02SO | SOT23-6 | 1 | D1213A-02SO-7 | Diodes Inc.
D502 | D1213A-02SO | SOT23-6 | 1 | D1213A-02SO-7 | Diodes Inc.
D503 | D1213A-02SO | SOT23-6 | 1 | D1213A-02SO-7 | Diodes Inc.
D601 | PACDN042 | SOT23-3 | 1 | PACDN042Y3R | onsemi
D602 | D1213A-02SO | SOT23-6 | 1 | D1213A-02SO-7 | Diodes Inc.
D701 |  | SOD128 | 1 | CMS05(TE12L,Q,M) | Toshiba
D702 |  | SOD128 | 1 | CMS05(TE12L,Q,M) | Toshiba
D703 |  | SOD128 | 1 | CMS05(TE12L,Q,M) | Toshiba
D704 |  | SOD128 | 1 | CMS05(TE12L,Q,M) | Toshiba
F101 | 0ZCM0010FF2G | 0603-RES | 1 | 0ZCM0010FF2G | Bel Fuse
F201 | 0ZCM0010FF2G | 0603-RES | 1 | 0ZCM0010FF2G | Bel Fuse
F202 | 0ZCM0010FF2G | 0603-RES | 1 | 0ZCM0010FF2G | Bel Fuse
F203 | 0ZCM0010FF2G | 0603-RES | 1 | 0ZCM0010FF2G | Bel Fuse
F204 | 0ZCM0010FF2G | 0603-RES | 1 | 0ZCM0010FF2G | Bel Fuse
F701 | 2920L600/16MR | 2920-FUSE | 1 | 2920L600/16MR | Littelfuse
FID901 | FIDUCIALUFIDUCIAL | MICRO-FIDUCIAL | 0
FID902 | FIDUCIALUFIDUCIAL | MICRO-FIDUCIAL | 0
FID903 | FIDUCIALUFIDUCIAL | MICRO-FIDUCIAL | 0
FID904 | FIDUCIALUFIDUCIAL | MICRO-FIDUCIAL | 0
FID905 | FIDUCIALUFIDUCIAL | MICRO-FIDUCIAL | 0
FID906 | FIDUCIALUFIDUCIAL | MICRO-FIDUCIAL | 0
FID907 | FIDUCIALUFIDUCIAL | MICRO-FIDUCIAL | 0
J101 | M20X2_PTH | M20X2_PTH | 1 | PPPC202LFBN-RC | Sullins
J102 | M04X1_JST_SH_RA | M04X1_JST_SH_SM_RA | 1 | SM04B-SRSS-TB(LF)(SN) | JST | PRT-14417 | SparkFun
J103 | M04X1_JST_SH_RA | M04X1_JST_SH_SM_RA | 1 | SM04B-SRSS-TB(LF)(SN) | JST | PRT-14417 | SparkFun
J201 | M04X1_JST_SH_RA | M04X1_JST_SH_SM_RA | 1 | SM04B-SRSS-TB(LF)(SN) | JST | PRT-14417 | SparkFun
J202 | M04X1_JST_SH_RA | M04X1_JST_SH_SM_RA | 1 | SM04B-SRSS-TB(LF)(SN) | JST | PRT-14417 | SparkFun
J203 | USB-MICRO | USB-MICRO | 1 | 10118194-0001LF | Amphenol Communications Solutions
J204 | M04X2_0.050_SMD_NO_CREAM | M04X2_0.050_SMD_NO_CREAM | 0
J205 | M04X2_0.050_SMD_NO_CREAM | M04X2_0.050_SMD_NO_CREAM | 0
J206 |  | MOLEX-1X3 | 1 | 22-11-2032 | Molex
J207 | M03X1_JST_SH | M03X1_JST_SH_SM | 1 | BM03B-SRSS-TB | JST
J208 |  | MOLEX-1X3 | 1 | 22-11-2032 | Molex
J301 | M04X2_0.050_SMD_NO_CREAM | M04X2_0.050_SMD_NO_CREAM | 0
J302 | M03X2PTH | 2X3-NS | 1 | 67997-206HLF | Amphenol Communications Solutions
J303 | M05X2_SMD_0.050_NOCREAM | M05X2_0.050_SMD_NO_CREAM | 0
J304 | M05X2_SMD_0.050_NOCREAM | M05X2_0.050_SMD_NO_CREAM | 0
J401 | M20X2_HARFLEX_M | M20X2_HARFLEX_M | 1 | 15150402601000 | HARTING Elektronik
J402 | M20X2_HARFLEX_M | M20X2_HARFLEX_M | 1 | 15150402601000 | HARTING Elektronik
J403 | M20X2_HARFLEX_M | M20X2_HARFLEX_M | 1 | 15150402601000 | HARTING Elektronik
J404 | M20X2_HARFLEX_M | M20X2_HARFLEX_M | 1 | 15150402601000 | HARTING Elektronik
J405 | M20X2_HARFLEX_M | M20X2_HARFLEX_M | 1 | 15150402601000 | HARTING Elektronik
J501 | SMA_MMCX_PTH_RA | MMCX_PTH_RA | 1 | 73415-1001 | Molex
J502 | SMA_MMCX_PTH_RA | MMCX_PTH_RA | 1 | 73415-1001 | Molex
J503 | SMA_MMCX_PTH_RA | MMCX_PTH_RA | 1 | 73415-1001 | Molex
J504 | SMA_MMCX_PTH_RA | MMCX_PTH_RA | 1 | 73415-1001 | Molex
J505 | SMA_MMCX_PTH_RA | MMCX_PTH_RA | 1 | 73415-1001 | Molex
J506 | SMA_MMCX_PTH_RA | MMCX_PTH_RA | 1 | 73415-1001 | Molex
J507 | U.FL | U.FL | 1 | 1909763-1 | TE Connectivity
J601 | USB-MICRO | USB-MICRO | 1 | 10118194-0001LF | Amphenol Communications Solutions
J602 | M04X2_0.050_SMD_NO_CREAM | M04X2_0.050_SMD_NO_CREAM | 0
J603 | M13X2_0.050_SHF_NO_CREAM | M13X2_0.050_SHF_NO_CREAM | 0
J604 | M07X1_PTH | M07X1_PTH | 1 | PPPC071LFBN-RC | Sullins
J701 | M04X2_SHROUDED | M04X2-SHROUDED | 1 | 75869-332LF | Amphenol Communications Solutions
J702 | POWERJACK_PJ051AH | PJ051AH | 1 | PJ-051AH | Same Sky
J901 | M05X2_SMD_0.050_NOCREAM | M05X2_0.050_SMD_NO_CREAM | 0
LED101 | LTST-C191TBKT-5A | LED-0603 | 1 | LTST-C191TBKT-5A | Lite-On
LED102 | LTST-C191KGKT | LED-0603 | 1 | LTST-C191KGKT | Lite-On
LED201 | LTST-C191KRKT | LED-0603 | 1 | LTST-C191KRKT | Lite-On
LED202 | LTST-C191KGKT | LED-0603 | 1 | LTST-C191KGKT | Lite-On
LED203 | LTST-C191KSKT | LED-0603 | 1 | LTST-C191KSKT | Lite-On
LED301 | LTST-C191KRKT | LED-0603 | 1 | LTST-C191KRKT | Lite-On
LED302 | LTST-C191KGKT | LED-0603 | 1 | LTST-C191KGKT | Lite-On
LED303 | LTST-C191TBKT-5A | LED-0603 | 1 | LTST-C191TBKT-5A | Lite-On
LED304 | LTST-C191KSKT | LED-0603 | 1 | LTST-C191KSKT | Lite-On
LED305 | LTST-C191KRKT | LED-0603 | 1 | LTST-C191KRKT | Lite-On
LED306 | LTST-C191KGKT | LED-0603 | 1 | LTST-C191KGKT | Lite-On
LED601 | LTST-C191KSKT | LED-0603 | 1 | LTST-C191KSKT | Lite-On
LED602 | LTST-C191KGKT | LED-0603 | 1 | LTST-C191KGKT | Lite-On
LED603 | LTST-C191KRKT | LED-0603 | 1 | LTST-C191KRKT | Lite-On
LED604 | LTST-C191KGKT | LED-0603 | 1 | LTST-C191KGKT | Lite-On
LED605 | LTST-C191KRKT | LED-0603 | 1 | LTST-C191KRKT | Lite-On
LED606 | LTST-C191KRKT | LED-0603 | 1 | LTST-C191KRKT | Lite-On
LED901 | LTST-C191KGKT | LED-0603 | 1 | LTST-C191KGKT | Lite-On
LF501 | FERRITE1206 | 1206 | 1 | MH3261-601Y | Bourns
LF601 | FERRITE0603 | 0603-FER | 1 | BLM18PG121SN1D | Murata
LF602 | FERRITE0603 | 0603-FER | 1 | BLM18PG121SN1D | Murata
LF603 | FERRITE1206 | 1206 | 1 | MH3261-601Y | Bourns
LF701 | FERRITE1206 | 1206 | 1 | MH3261-601Y | Bourns
LS601 | PKMCS0909E4000-R1 | XDCR_PKMCS0909E4000-R1 | 1 | PKMCS0909E4000-R1 | Murata
Q201 | MOSFET-NCHANNELSMD | SOT23-3 | 1 | DMG3402L-7 | Diodes Inc.
Q202 | MOSFET-NCHANNELSMD | SOT23-3 | 1 | DMG3402L-7 | Diodes Inc.
Q701 | MOSFET-NCHANNELSMD | SOT23-3 | 1 | DMG3402L-7 | Diodes Inc.
Q702 | MOSFET-PCHANNEL_SO8 | SO08 | 1 | SI4431CDY-T1-GE3 | Vishay
R1003 | 470 | 0402-RES | 1 | RC0402FR-07470RL | Yageo
R101 | 10k | 0402-RES | 1 | RC0402FR-0710KL | Yageo
R102 | 10k | 0402-RES | 1 | RC0402FR-0710KL | Yageo
R103 | 10k | 0402-RES | 1 | RC0402FR-0710KL | Yageo
R104 | 470 | 0402-RES | 1 | RC0402FR-07470RL | Yageo
R105 | 470 | 0402-RES | 1 | RC0402FR-07470RL | Yageo
R201 | 1k | 0402-RES | 1 | RC0402FR-071KL | Yageo
R202 | DNP | 0402-RES | 0
R203 | 10k | 0402-RES | 1 | RC0402FR-0710KL | Yageo
R204 | 10k | 0402-RES | 1 | RC0402FR-0710KL | Yageo
R205 | 100k | 0402-RES | 1 | RC0402FR-07100KL | Yageo
R206 | 47k | 0402-RES | 1 | RC0402FR-0747KL | Yageo
R207 | 10k | 0402-RES | 1 | RC0402FR-0710KL | Yageo
R208 | 10k | 0402-RES | 1 | RC0402FR-0710KL | Yageo
R209 | 27 | 0402-RES | 1 | RC0402FR-0727RL | Yageo
R210 | 10k | 0402-RES | 1 | RC0402FR-0710KL | Yageo
R211 | 27 | 0402-RES | 1 | RC0402FR-0727RL | Yageo
R212 | DNP | 0402-RES | 0
R213 | 1.2k | 0402-RES | 1 | RC0402FR-071K2L | Yageo
R214 | DNP | 0402-RES | 0
R215 | 470 | 0402-RES | 1 | RC0402FR-07470RL | Yageo
R216 | 470 | 0402-RES | 1 | RC0402FR-07470RL | Yageo
R217 | 100k | 0402-RES | 1 | RC0402FR-07100KL | Yageo
R218 | 10k | 0402-RES | 1 | RC0402FR-0710KL | Yageo
R219 | 470 | 0402-RES | 1 | RC0402FR-07470RL | Yageo
R220 | 470 | 0402-RES | 1 | RC0402FR-07470RL | Yageo
R221 | 100k | 0402-RES | 1 | RC0402FR-07100KL | Yageo
R222 | 470 | 0402-RES | 1 | RC0402FR-07470RL | Yageo
R223 | 100 | 0402-RES | 1 | RC0402FR-07100RL | Yageo
R224 | 100 | 0402-RES | 1 | RC0402FR-07100RL | Yageo
R225 | 100k | 0402-RES | 1 | RC0402FR-07100KL | Yageo
R226 | 470 | 0402-RES | 1 | RC0402FR-07470RL | Yageo
R227 | 100k | 0402-RES | 1 | RC0402FR-07100KL | Yageo
R228 | 470 | 0402-RES | 1 | RC0402FR-07470RL | Yageo
R301 | 10k | 0402-RES | 1 | RC0402FR-0710KL | Yageo
R302 | 10k | 0402-RES | 1 | RC0402FR-0710KL | Yageo
R303 | DNP | 0402-RES | 0
R304 | DNP | 0402-RES | 0
R305 | 10k | 0402-RES | 1 | RC0402FR-0710KL | Yageo
R306 | 10k | 0402-RES | 1 | RC0402FR-0710KL | Yageo
R307 | 10k | 0402-RES | 1 | RC0402FR-0710KL | Yageo
R308 | 470 | 0402-RES | 1 | RC0402FR-07470RL | Yageo
R309 | 470 | 0402-RES | 1 | RC0402FR-07470RL | Yageo
R310 | 470 | 0402-RES | 1 | RC0402FR-07470RL | Yageo
R311 | 470 | 0402-RES | 1 | RC0402FR-07470RL | Yageo
R312 | 10k | 0402-RES | 1 | RC0402FR-0710KL | Yageo
R313 | 470 | 0402-RES | 1 | RC0402FR-07470RL | Yageo
R314 | 470 | 0402-RES | 1 | RC0402FR-07470RL | Yageo
R401 | 0 | 0603-RES | 1 | RC0603FR-100RL | Yageo
R402 | DNP | 0603-RES | 0
R403 | 0 | 0603-RES | 1 | RC0603FR-100RL | Yageo
R404 | DNP | 0603-RES | 0
R405 | 0 | 0603-RES | 1 | RC0603FR-100RL | Yageo
R406 | DNP | 0603-RES | 0
R407 | 0 | 0603-RES | 1 | RC0603FR-100RL | Yageo
R408 | DNP | 0603-RES | 0
R501 | 1k | 0402-RES | 1 | RC0402FR-071KL | Yageo
R502 | 82 | 0402-RES | 1 | RC0402FR-0782RL | Yageo
R503 | DNP | 0805 | 0
R504 | 10k | 0402-RES | 1 | RC0402FR-0710KL | Yageo
R505 | 1k | 0402-RES | 1 | RC0402FR-071KL | Yageo
R506 | 82 | 0402-RES | 1 | RC0402FR-0782RL | Yageo
R507 | DNP | 0805 | 0
R508 | 10k | 0402-RES | 1 | RC0402FR-0710KL | Yageo
R509 | 100 | 0402-RES | 1 | RC0402FR-07100RL | Yageo
R510 | DNP | 0805 | 0
R511 | 10k | 0402-RES | 1 | RC0402FR-0710KL | Yageo
R512 | 100 | 0402-RES | 1 | RC0402FR-07100RL | Yageo
R513 | DNP | 0805 | 0
R514 | 10k | 0402-RES | 1 | RC0402FR-0710KL | Yageo
R515 | 100 | 0402-RES | 1 | RC0402FR-07100RL | Yageo
R516 | DNP | 0805 | 0
R517 | 10k | 0402-RES | 1 | RC0402FR-0710KL | Yageo
R518 | DNP | 0805 | 0
R519 | 10k | 0402-RES | 1 | RC0402FR-0710KL | Yageo
R520 | 100 | 0402-RES | 1 | RC0402FR-07100RL | Yageo
R521 | 100 | 0402-RES | 1 | RC0402FR-07100RL | Yageo
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

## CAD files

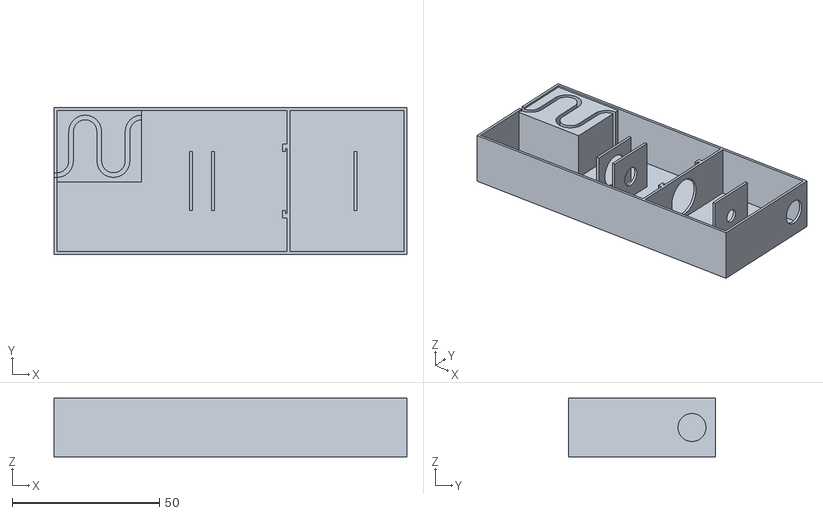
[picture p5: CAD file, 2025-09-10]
Box/box.stl
120.0 x 50.0 x 20.0

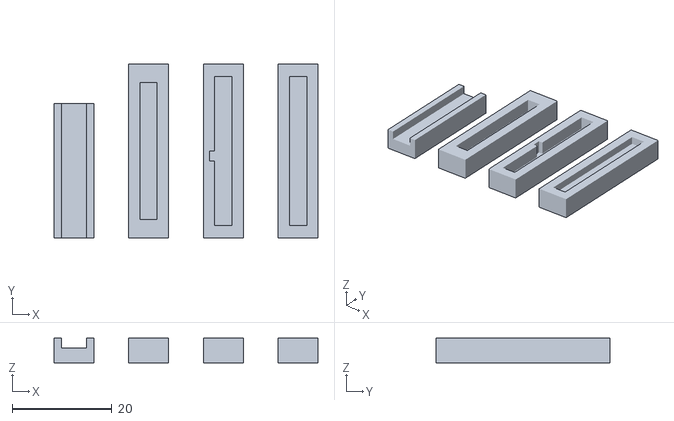
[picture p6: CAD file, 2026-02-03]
Crimp_Jigs/crimps.stl
53.0 x 35.0 x 5.00

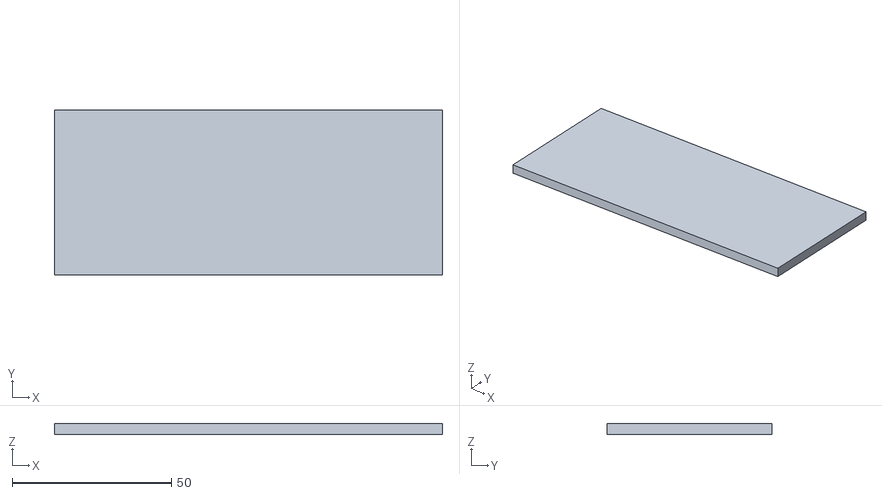
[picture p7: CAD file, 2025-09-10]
Box/lid.stl
122.0 x 52.0 x 3.50

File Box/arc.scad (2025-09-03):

module sector(radius, angles, fn = 24) {
    r = radius / cos(180 / fn);
    step = -360 / fn;

    points = concat([[0, 0]],
        [for(a = [angles[0] : step : angles[1] - 360]) 
            [r * cos(a), r * sin(a)]
        ],
        [[r * cos(angles[1]), r * sin(angles[1])]]
    );

    difference() {
        circle(radius, $fn = fn);
        polygon(points);
    }
}

module arc(radius, angles, width, fn = 24) {
    difference() {
        sector(radius + width, angles, fn);
        sector(radius, angles, fn);
    }
} 

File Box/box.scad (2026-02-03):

//
// dark box for optode testing
//
include <arc.scad>

e = 0.1;
mm = 25.4;
$fn = 128;

// optode dims
op_lg_dia = 12;
op_lg_len = 10.5;
op_sm_dia = 7;
op_sm_len = 6.5;
op_over = 0.5;			/* oversize for optode mounting holes */

// box dims
box_len = 120;
box_wid = 50;
box_hgt = 20;
box_thk = 1;

op_off = box_len*0.5;			/* optode position from box end */
op_bkt_wid = 20;		/* optode bracket width */
op_bkt_thk = 1;			/* optode bracket thickness */

op_bkt_offset = box_wid/2-op_bkt_wid/2;

cable_dia = 1.6;		/* slot width for cable */

// cable exit
ct_rad = 4;
ct_leng = 10;
ct_hgt = box_hgt-box_thk-cable_dia;

// Filter holder
filter_pos = box_len*0.66;
filter_wid = 25;
filter_hole_dia = 15;

filter_w1 = 1.5;
filter_w2 = 2.5;
filter_thk = 0.75;

// LED holder
led_pos = box_len*0.85;
led_dia = 5;

module filter_slot() {
     translate( [filter_pos, 0, 0]) {
	  difference() {
	       cube( [box_thk, box_wid, box_hgt]);
	       translate( [-e, box_wid/2, box_hgt/2])
		    rotate( [0, 90, 0])
		    cylinder( d=filter_hole_dia, h=box_thk+2*e);
	  }
	  translate( [-filter_thk+e, box_wid/2-filter_wid/2, 0]) {
	       difference() {
		    cube( [filter_thk, filter_wid, box_hgt]);
		    translate( [-e, filter_w1, 0])
			 cube( [filter_thk+2*e, filter_wid-2*filter_w1, box_hgt+e]);
	       }
	       translate( [-box_thk+e, 0, 0]) {
		    difference() {
			 cube( [box_thk, filter_wid, box_hgt]);
			 translate( [-e, filter_w2, 0])
			      cube( [box_thk+2*e, filter_wid-2*filter_w2, box_hgt+e]);
		    }
	       }
	  }
     }
}

module led_bracket() {
  translate( [led_pos, op_bkt_offset, 0]) {
    difference() {
      cube( [op_bkt_thk, op_bkt_wid, box_hgt]);
      translate( [-e, op_bkt_wid/2, box_hgt/2])
	rotate( [0, 90, 0])
	cylinder( d=led_dia+0.2, h=op_bkt_thk+2*e);
    }
  }
}

module optode() {
  cylinder( h=op_sm_len, d=op_sm_dia);
  translate( [0, 0, op_sm_len-e])
    cylinder( h=op_lg_len, d=op_lg_dia);
}

module empty_box() {
  difference() {
    cube( [box_len, box_wid, box_hgt]);
    translate( [box_thk, box_thk, box_thk])
      cube( [box_len-2*box_thk, box_wid-2*box_thk, box_hgt]);
  }
}


module op_bracket() {
  translate( [op_off-op_lg_len-op_sm_len+3, op_bkt_offset, 0]) {
    difference() {
      cube( [op_bkt_thk, op_bkt_wid, box_hgt]);
      translate( [-e, op_bkt_wid/2, box_hgt/2])
	rotate( [0, 90, 0])
	cylinder( d=op_lg_dia+op_over, h=op_bkt_thk+2*e);
    }
  }
  translate( [op_off-op_sm_len+e, op_bkt_offset, 0]) {
    difference() {
      cube( [op_bkt_thk, op_bkt_wid, box_hgt]);
      translate( [-e, op_bkt_wid/2, box_hgt/2])
	rotate( [0, 90, 0])
	cylinder( d=op_sm_dia+op_over, h=op_bkt_thk+2*e);
    }
  }
}

module serpent( nturn) {

  for( i=[0:nturn-1]) {
    translate( [i*4*ct_rad+i*2*cable_dia, 0, 0]) {
      linear_extrude(ct_hgt+e) arc(ct_rad, [180, 360], cable_dia);
      translate( [ct_rad*2+cable_dia, ct_leng, 0])
	linear_extrude(ct_hgt+e) arc(ct_rad, [0, 180], cable_dia);
      translate( [ct_rad, -e, 0])
	cube( [cable_dia, ct_leng+2*e, ct_hgt+e]);
      translate( [ct_rad*3+cable_dia, -e, 0])
	cube( [cable_dia, ct_leng+2*e, ct_hgt+e]);
    }    
  }
}

function exit_wid( nturn) = ct_leng+(ct_rad+cable_dia)*2+2*cable_dia;
function exit_hgt() = ct_hgt+box_thk;

module cable_exit( nturn) {
  // dims to enclose the serpent
  sd_len = nturn*ct_rad*4+cable_dia*nturn*2+cable_dia;
  sd_wid = ct_leng+(ct_rad+cable_dia)*2;
  translate( [-ct_rad-cable_dia, cable_dia, box_thk]) {
    difference() {
      translate( [ct_rad+cable_dia, -cable_dia, 0])
	cube( [sd_len-2*ct_rad-2*cable_dia, sd_wid+2*cable_dia, ct_hgt-e]);
      translate( [ct_rad+cable_dia, ct_rad+cable_dia, -e])
	serpent( nturn);
    }
  }
  cube( [sd_len-2*ct_rad-2*cable_dia, sd_wid+2*cable_dia, box_thk+e]);
}


module op_with_bracket() {
// move to optode position
  translate( [op_off, op_bkt_offset+op_bkt_wid/2, box_hgt/2]) {
    rotate( [0, -90, 0])  {
      //      color("#606060")    optode();
    }
  }
  // bracket
  op_bracket();
}

module box() {
  difference() {
    empty_box();
    // optode cable slot
    translate( [-e, box_wid-exit_wid(2)-box_thk+cable_dia, box_thk+cable_dia])
      cube( [box_wid+2*e, cable_dia, ct_hgt]);
    // LED BNC hole
    translate( [box_len-box_thk-e, box_wid-8, box_hgt/2])
	 rotate( [0, 90, 0])
	 cylinder( d=0.375*mm, h=box_thk+2*e);
  }
}

module box_assembly() {
     box();
     translate( [box_thk, box_wid-exit_wid(2)-box_thk, box_thk]) cable_exit(2);

     op_with_bracket();
     led_bracket();
     filter_slot();
}

lid_lip = 2.5;

module lid() {
     difference() {
	  translate( [-box_thk, -box_thk, e])
	       cube( [box_len+2*box_thk, box_wid+2*box_thk, lid_lip+box_thk]);
	  cube([box_len, box_wid, lid_lip+e]);
     }
}

// box_assembly();

rotate( [180, 0, 0]) lid();

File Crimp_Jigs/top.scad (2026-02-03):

//
// top crimp for Harting 40p connector
//
e = 0.1;
$fn = 32;
mm = 25.4;

slot_w = 5;
slot_d = 2;

body_w = 8;
body_l = 27;
body_d = 5;

extra_l = 35;

bslot_w = 3.4;
bslot_l = 27.5;
bslot_d = 3;

module top() {
  difference() {
    cube( [body_w, body_l, body_d]);
    translate( [(body_w-slot_w)/2, -e, body_d-slot_d])
      cube( [slot_w, body_l+2*e, slot_d+2*e]);
  }
}

module bot() {
  difference() {
    cube( [body_w, extra_l, body_d]);
    translate( [(body_w-bslot_w)/2, (extra_l-bslot_l)/2, body_d-bslot_d])
      cube( [bslot_w, bslot_l, bslot_d+2*e]);
  }
}

sbot_w = 3.6;
sbot_l = 30.3;
sbot_d = 3;

key_w = 1.2;
key_h = 2.2;

module sbot() {
  difference() {
    cube( [body_w, extra_l, body_d]);
    translate( [(body_w-sbot_w)/2, (extra_l-sbot_l)/2, body_d-sbot_d]) {
      cube( [sbot_w, sbot_l, sbot_d+e]);
      translate( [-key_w, (sbot_l/2)-key_h/2, 0])
	cube( [key_w+e, key_h, sbot_d+e]);
    }
  }
}

stop_d = 1.8;

module stop() {
  difference() {
    cube( [body_w, extra_l, body_d]);
    translate( [(body_w-sbot_w)/2, (extra_l-sbot_l)/2, body_d-stop_d]) {
      cube( [sbot_w, sbot_l, stop_d+e]);
    }
  }
}


top();
translate( [15, 0, 0]) bot();
translate( [30, 0, 0]) sbot();
translate( [45, 0, 0]) stop();

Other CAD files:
Crimp_Jigs/crimps2.stl

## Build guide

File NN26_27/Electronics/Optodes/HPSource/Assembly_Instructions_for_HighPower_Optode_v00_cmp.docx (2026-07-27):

# Assembly Instructions for NinjaNIRS High-Power Source Optodes

March 12th, 2026

# Required Materials

- Glue / Epoxy
  - G-S Hypo Cement (optional, can use transparent epoxy instead)
  - Loctite EA M-31CL Clear Epoxy
  - Loctite EA M-21HP Off-White Epoxy (or NIRx potting compound)
- Source PCB with mounted LEDs
- High NA light pipes
- NIRx NIRsport optode cable
- NIRx NIRsport optode shell
- Vise (https://www.stickvise.com) or equivalent
- Putty – XXX instead of vise and putty we might want to 3D print a jig XXX
- Syringe with large diameter blunt needle

# Step 1: Build Light-Pipe Pair

- Wipe the light pipes with alcohol. Make sure they are clean.
- Place light pipes in pairs in the vice. (see Figure 1.1)
- Apply a small amount of epoxy (M-31CL) or glue (G-S Hypo) between the two pipes of a pair. (see Figure 1.2)
- Let the glue cure before removing the pair from the vice.

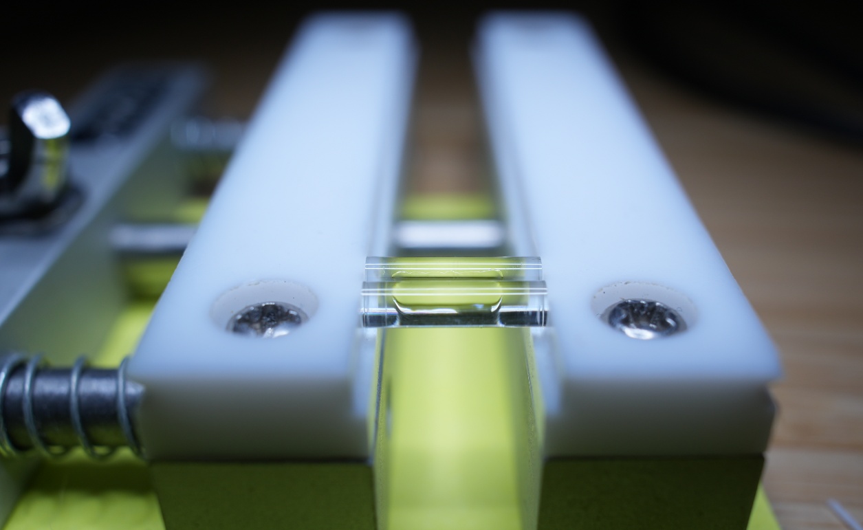
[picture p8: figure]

Figure 1.1: Pair of light pipes in vice.

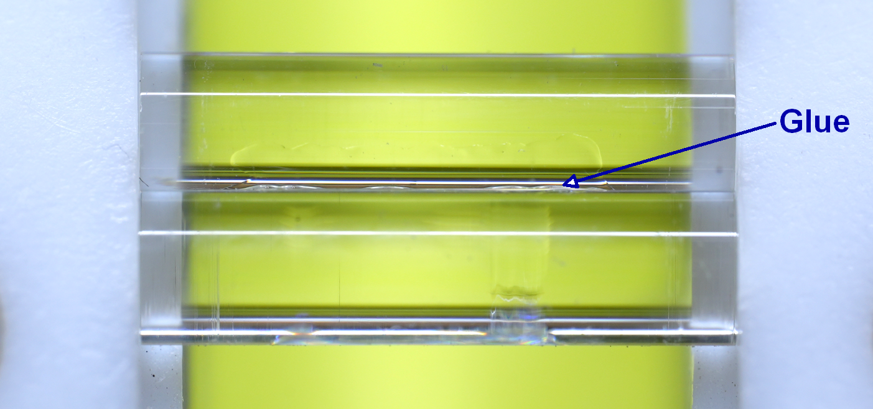
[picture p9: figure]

Figure 1.2: Pair of light pipes in vice with glue.

# Step 2: Glue the Pair of Light Pipes to the PCB

- Place a blob of transparent epoxy (M-31CL) on the PCB, with the PCB lying on a flat and horizontal surface. A toothpick or similar can be used to push the glue around the LEDs and into all gaps. (see Figure 2.1)
- Place the light pipe pair on top of the LEDs. Try to prevent large air bubbles around the LEDs and underneath the pipes. (see Figure 2.2)
- Align the pipes under a microscope to maximize LED die coverage. (see Figure 2.3)
- Let the epoxy cure. Make sure no one touches or moves the pipes during the curing period!!

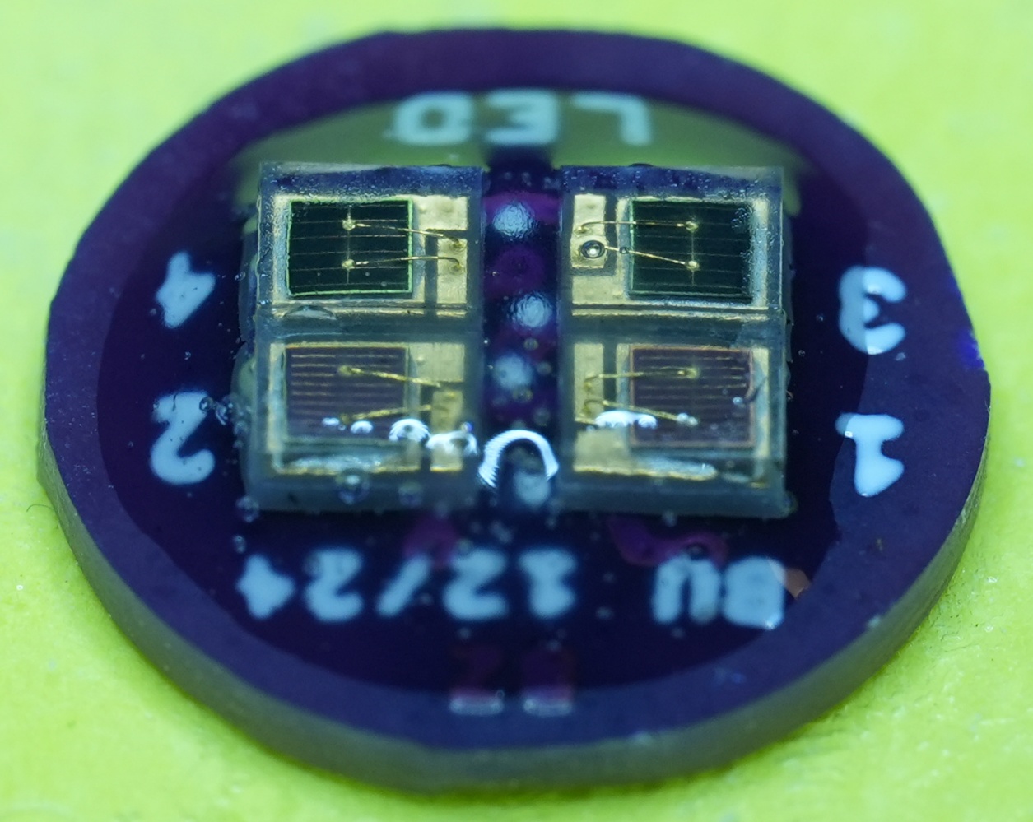
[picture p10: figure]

Figure 2.1: Blob of epoxy on PCB.

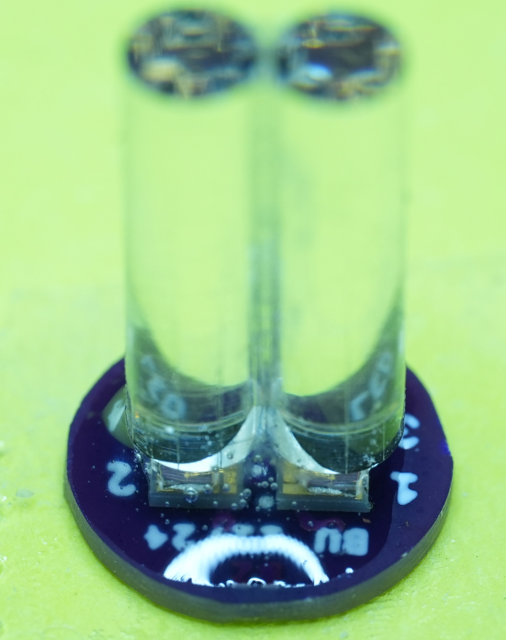
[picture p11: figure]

Figure 2.2: Light pipe pair on top of PCB.

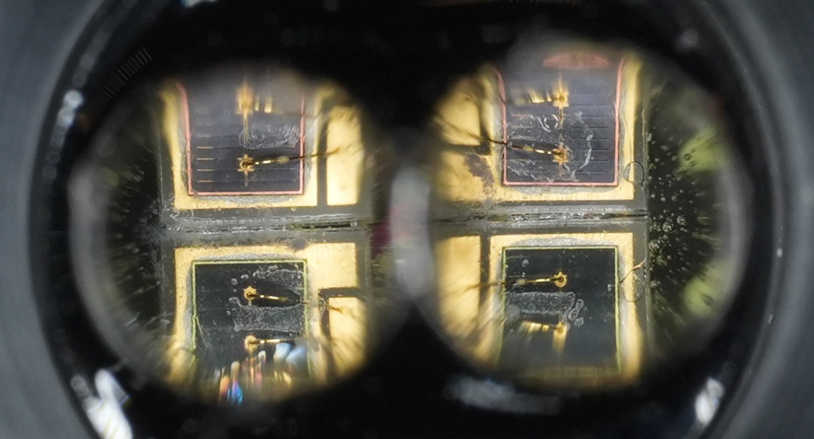
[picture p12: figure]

Figure 2.3: Light pipe alignment under microscope.

# Step 3: Solder the NIRx Optode Cable to the PCB

- Solder the NIRx optode wire to the back of the PCB. (see Figure 3.1)
- XXX need to add a schematic or picture including the 4 pin connector here as sometimes the colors of the NIRx wires change XXX

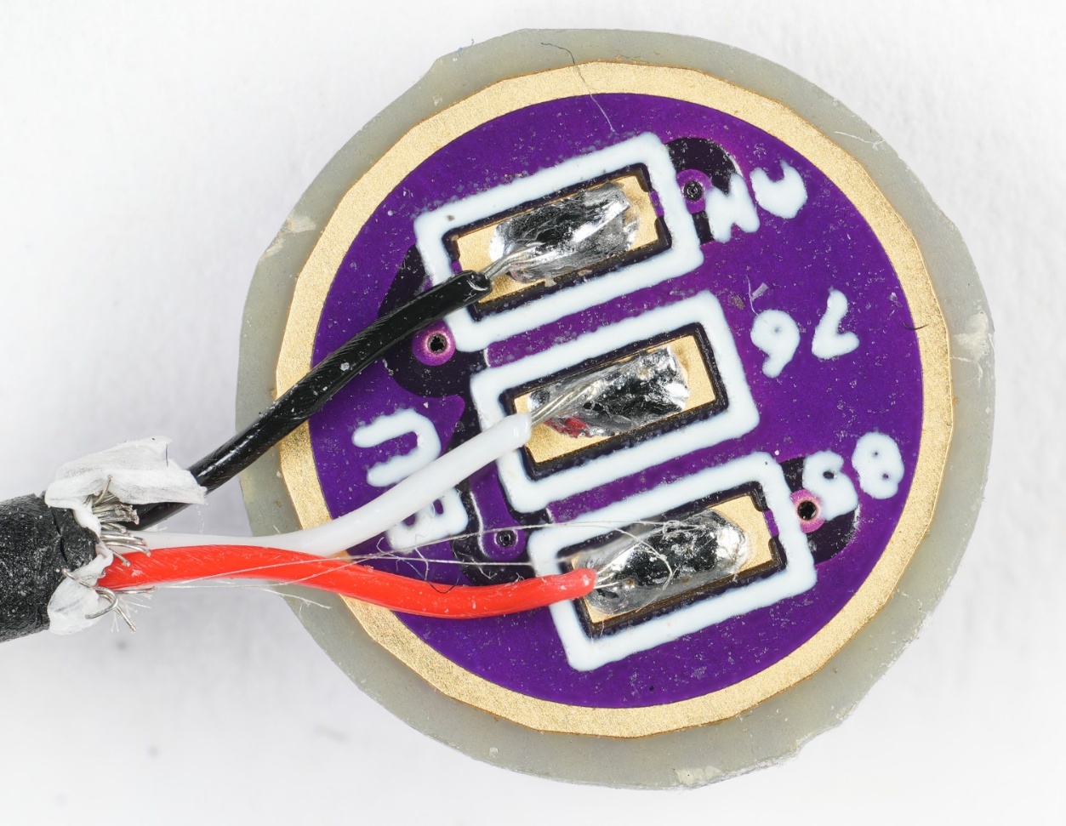
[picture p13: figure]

Figure 3.1: Wires soldered to PCB.

# Step 4: Pot the PCB Assembly in NIRx Optode Shell

- Clamp the light pipe pair with glued on PCB in the vise. Center the NIRx optode shell and fix it using putty. (see Figure 4.1)
- Fix the PCB inside the shell using small amounts of epoxy (M-21HP). Let the epoxy cure. (see Figure 4.2)
- Completely pot the back side of the using potting medical grade epoxy (M-21HP). Make sure the wire is well embedded in epoxy and fixed in the notch of the optode shell. Let it cure.
- Pot the front side of the optode using medical grade epoxy (M-21HP or M-31CL). Using a syringe, fill the volume inside the optode slowly to avoid air pockets. Let it cure. (see Figure 4.3)

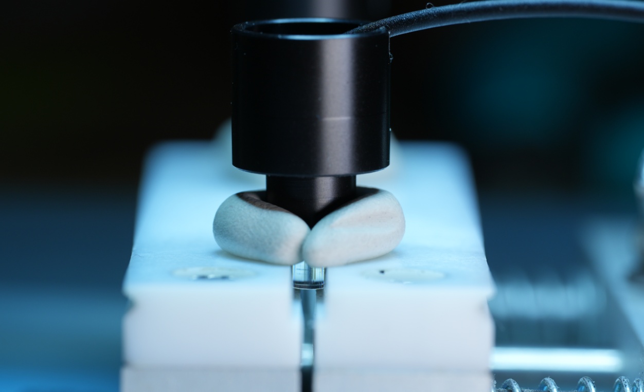
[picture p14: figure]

Figure 4.1: Light pipe pair centered in optode shell.

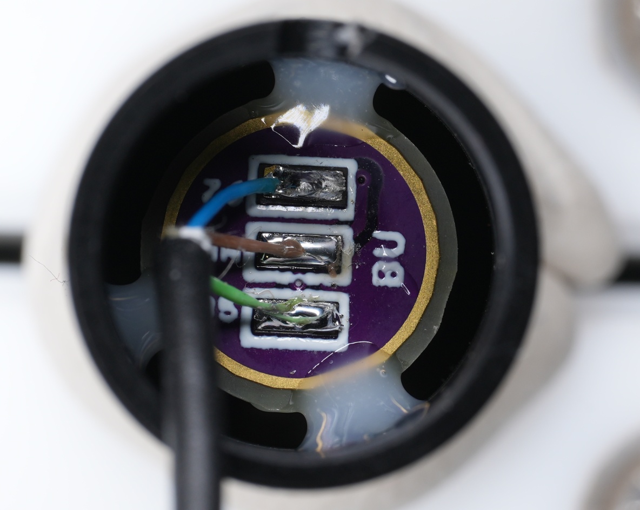
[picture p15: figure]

Figure 4.2: Fixation of PCB inside shell using epoxy.

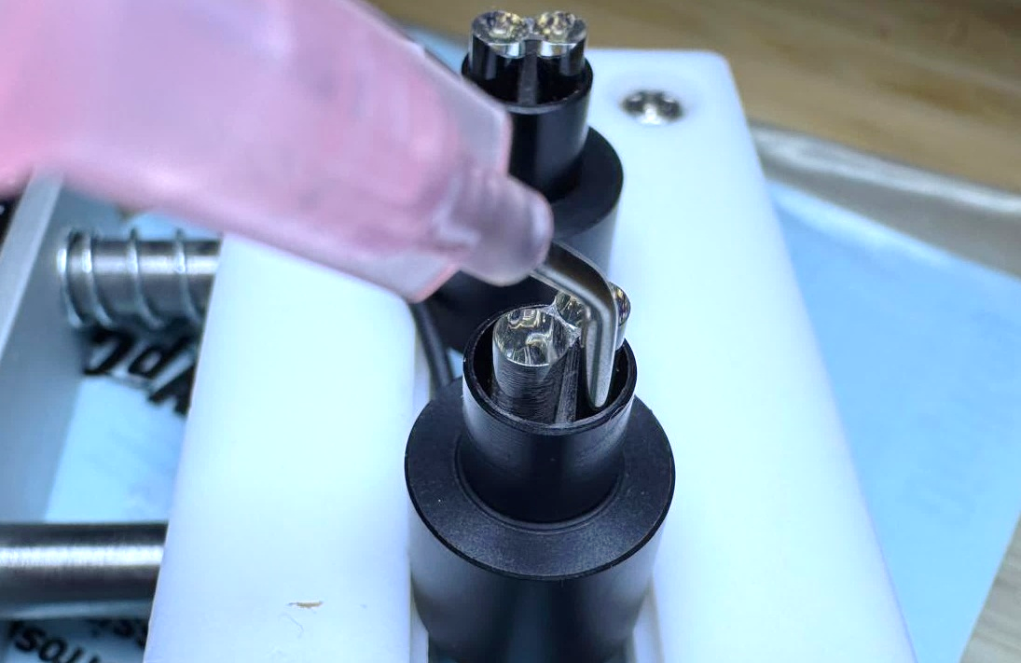
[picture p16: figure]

Figure 4.3: Potting of optode front side.

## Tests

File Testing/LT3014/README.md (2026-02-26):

# Testing of LT3014 board

The board works OK more or less as designed.
<br>(new items added at bottom)

ECOs:
* Need to install R13, R14 as 100 ohms and C10 as 1uf for stability
* C4 and C5 need to be rated for > 60V (prototype built with 10V parts)

## 2025-06-02

The main issue is time to switch on and off may be slow for use in the
system if we want to change voltage dynamically.

With the default values, there is a resistive load of 210k (R9, R10)
in parallel with the voltage adjust resistor chain (about 2.5M).
There is an output capaictor (C5) of 1.0uF on the LT3014 output.

See [no_load.png](no_load.png).  Rise and fall times are about 2ms.

The fall time is dependent on the load resistor.  Here are some
measurements taken with 50V caps installed at C4, C5 and the supply
voltage reduced to 50V.  Note that R9 was disconnected, so the only
built-in load is the 2.5M adjust chain.  Voltage swing is from 46 to
36V.

| Load R | Equivalent R | 10V fall time     |              |
|--------|--------------|-------------------|--------------|
|        |              | <b>C5 = 1.0uF</b> | <b>4.7uF</b> |
| 500k   | 420k         | 9.2ms             | 16.6ms       |
| 1M     | 715k         | 15ms              |              |
| 2.5M   | 2.5M         | 47ms              | 85ms         |

If the time constant were due only discharge of C5 through the load
resistor, we would expect a much longer time constant.  For example
for the 420k case to dischage 1.0uF by 10V should take 85ms.

So my theory is that there is feedback in U1 which drains the output
capacitor.

Let's try changing C5 to a larger value.  Updated the table above.
Interestingly, not a factor of 4.7.  So this supports the theory that
it is not just the R-C of output capacitor and load.

## 2025-06-11

Change R9 to 512k and R10 to 24k to decrease load from voltage sense.
(also change C5 back to 1.0uF 50V).  Power supply at 50V.
Looks OK with about 5% error.

Also rise time is ~3ms (R-C curve) and fall time is 10ms (ramp)
for a 10V step.

| R9   | DPOT | V_MON | Multimeter | VSENSE TP | ERR PCT |
|------|------|-------|------------|-----------|---------|
| 510k | 0    | 29.6  | 31.2       | 1.40      | -5%     |
|      | 256  | 33.6  | 35.5       | 1.59      | -5%     |
|      | 512  | 38.9  | 41.1       | 1.85      | -5%     |
|      | 768  | 46.1  | 49.1       | 2.21      | -6%     |
|      |      |       |            |           |         |

## 2026-02-12

Studying load regulation.  Add a little MOSFET switch
to change the load (at 60V) from 640uA to 1.3mA.
This is similar to a large SiPM signal.

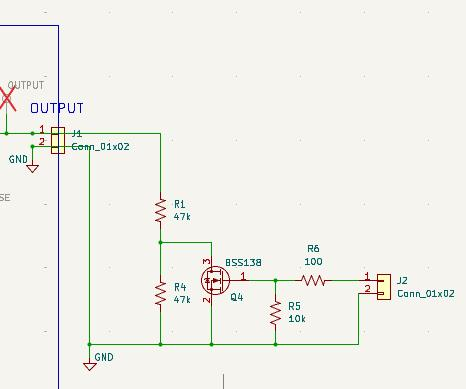
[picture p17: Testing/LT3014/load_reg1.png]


Here's a plot of the voltage at the output.
<br>__NOTE__ Scope AC-coupling with a time constant
of ~15ms (according to the internet) used.

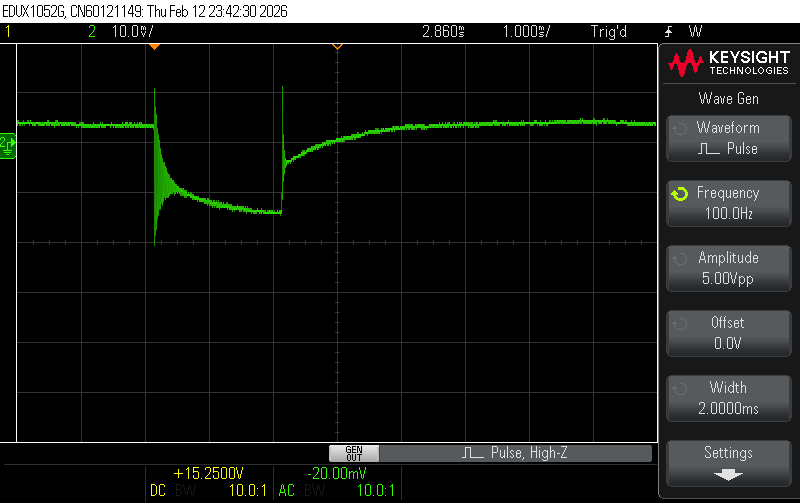
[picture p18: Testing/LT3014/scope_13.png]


## 2026-02-18

Add 150 ohms in series with 680nF on output to simulate
all the SiPM filter networks in series.

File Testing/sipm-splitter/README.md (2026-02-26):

(new items added at bottom)

**2026-02-03**

Crosstalk tests.  Channels 1-4 change TIA feeback cap from 1000pF to
470pF to eliminate 50MHz oscillations.  

Pulse red LED through 330 ohms into S13360-3050PE (ch 2) at 50Hz for
1.2ms at 3.38V amplitude (adjusted to give 5V on ch 2).
<br>Bias set at 56V.

<br>View signal on S13360-3025PE (ch 1)
<br>Observe bipolar crosstalk peaks of ~100uS but <1mV during body of pulse

Scope set to average 32 traces with BWL enabled.

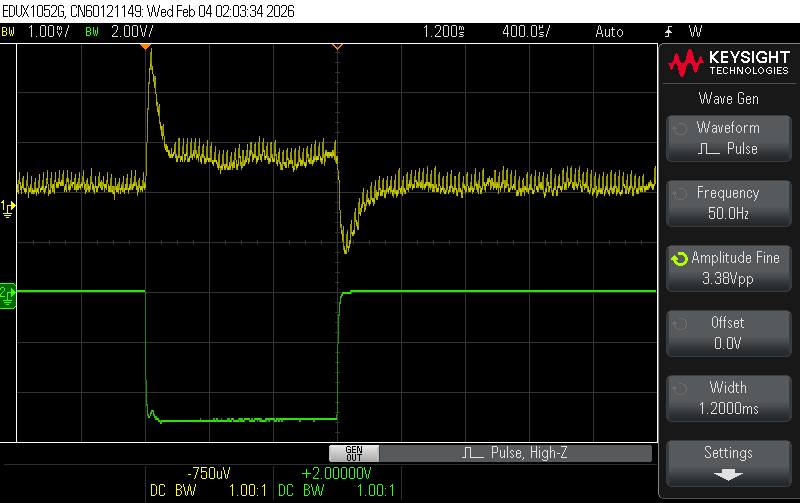
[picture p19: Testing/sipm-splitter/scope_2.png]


Looking at V(bias).

First is bias on pulsed SiPM. There is a drop of about 400mV which is
likely due to the drop in the 1k series resistor feeding each SiPM.

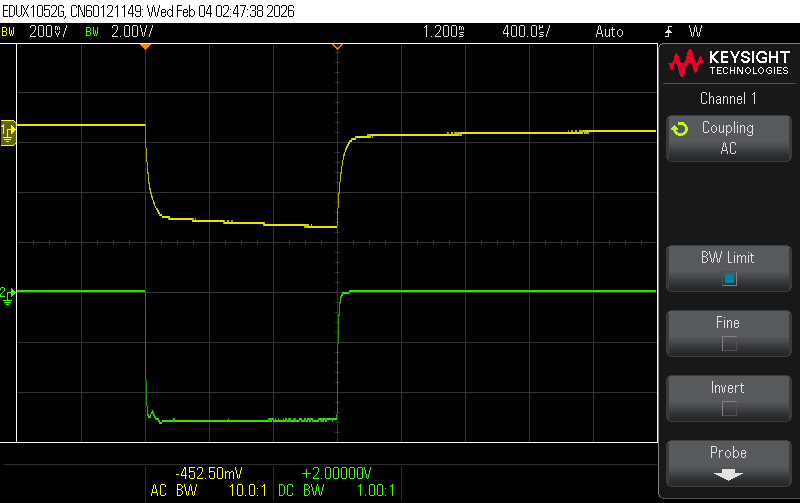
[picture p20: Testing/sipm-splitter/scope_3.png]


Next is main bias rail with pulser reset to 10Hz.  There are some
fairly wild excursions on the regulated bias voltage.  Obviously
the regulator (LT3014) is not completely stable.

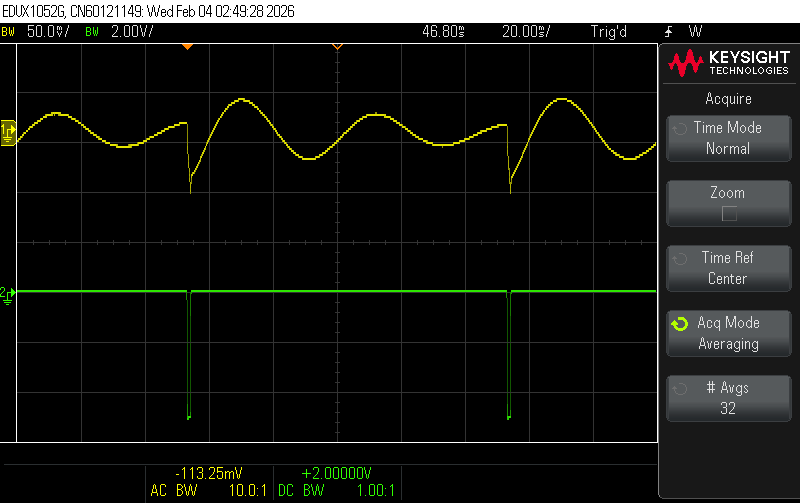
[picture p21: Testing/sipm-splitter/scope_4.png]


Same thing with pulse rate reduced to 1Hz.  The ringing is damped and
eventually settles down after about 300ms.

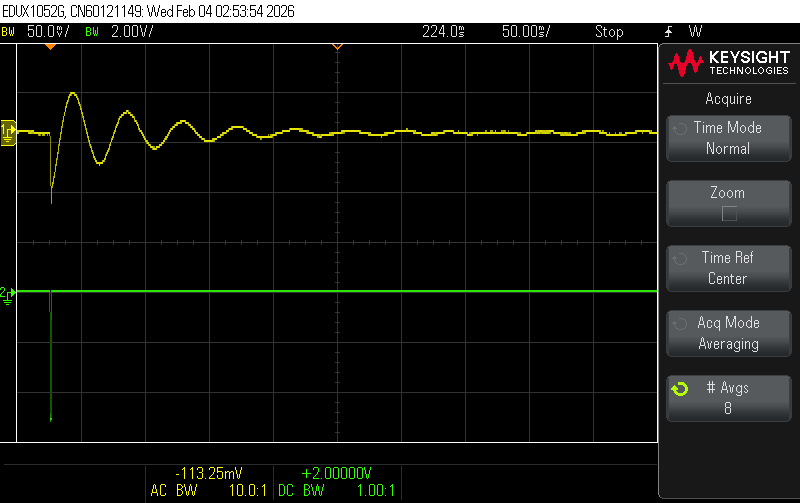
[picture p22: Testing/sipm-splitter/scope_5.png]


Note that looking at the raw boost converter (U4-1) there is no perturbation,
and the output of U4 (pin 5) looks the same as above (they are connected
together through copper).

So there is a perturbation on entire bias network of around 100mV peak-to-peak
when a large signal is generated on one SiPM.  This will change the SiPM
gain by a few percent.

**2026-02-05**

Investigating the bias supply issues.  Pulse producing a 5V output on the TIA.
This implies 5V/15k = 333uA out of the SiPM.  Observe about 400mV drop on the 1k
series R in the filter, so this is consistent.

Gain supposed to be 1.7e6 @PDE=40%.  So photocurrent would be ~200pA.

Looking at Vbias ringing.  Double C12 to 2uF.  No visible change.
Add 4.7uF in parallel for total 6.7uF.  Still no change.

Disconnect digital pot and jumper 10k from R20 bottom to GND.
Still no visible change.

Finally, remove C12 (and restore Digi-pot).  Still no change!

Try bypassing R17 with some C:
* 4.7pF - no change
* 47pF - no change
* 470pF - no change
* 4.7nF - aha!  Now a bit under-damped.

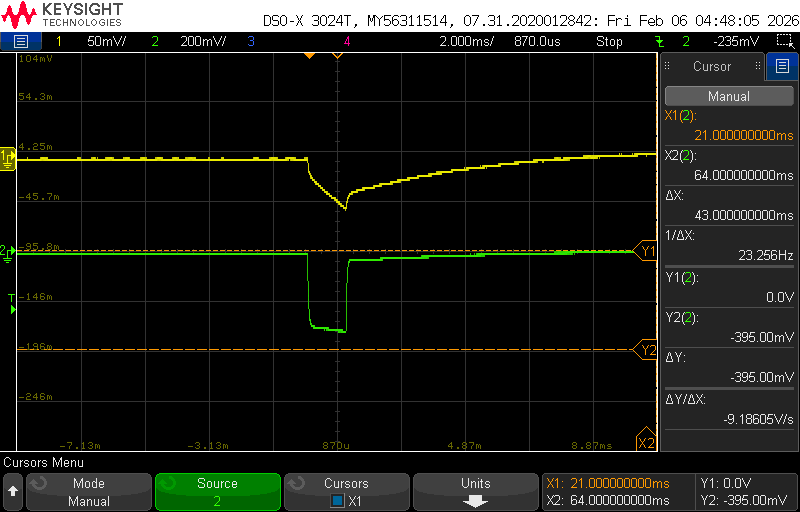
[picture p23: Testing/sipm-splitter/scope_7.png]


**2026-02-10**

Continuing testing.  Another shot with 4.7nF.  Note that stimulated SiPM is in ch 2.
Scope probes are on ends of R43 (Vbias, SiPM#2 K).

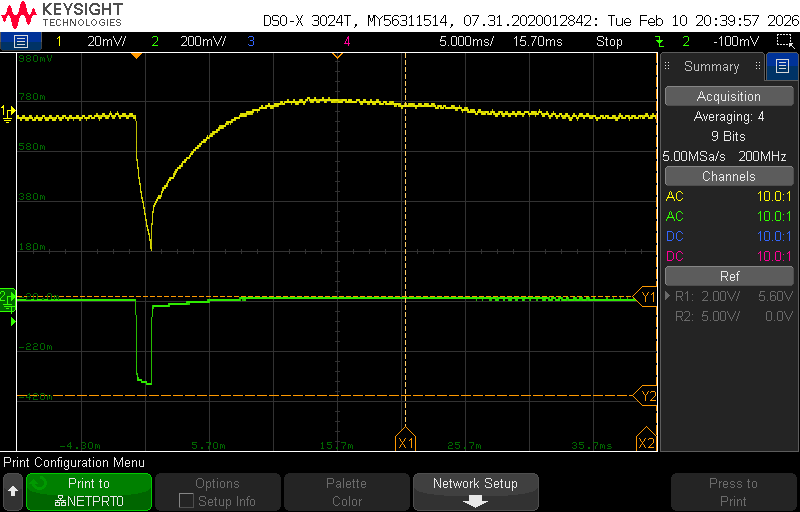
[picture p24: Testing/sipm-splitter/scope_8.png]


Change C to 1nF.  Note change in horizontal scale.

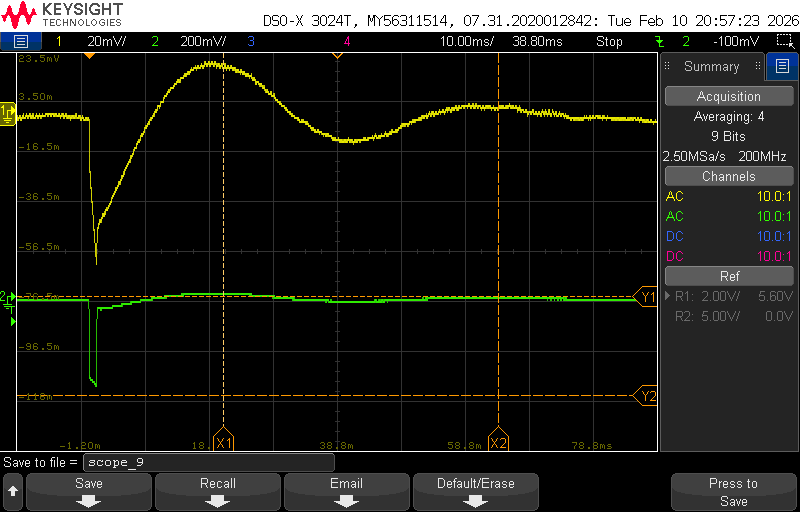
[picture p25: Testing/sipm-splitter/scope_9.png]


Change C to 2.2nF.

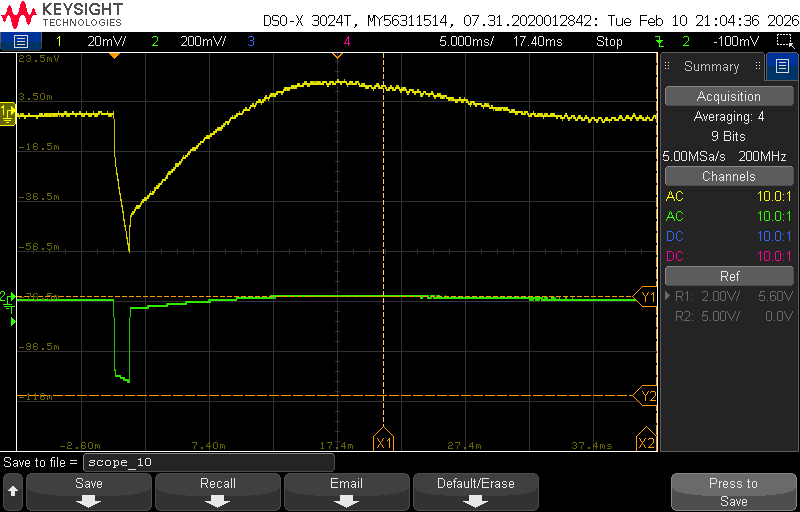
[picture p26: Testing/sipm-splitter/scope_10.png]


Change C to 3.3nF





**2026-02-11**

Move over to LT3014 test log for some experimentation.

**2026-02-26**

Remove C15 ("soft start") C.  Otherwise same test conditions.

.

Now the perturbation is < 10mV.  Should re-optimize the compensation C now.

Remove the Cap.  Now we see about 30mV.

.

Back to 3.3nF



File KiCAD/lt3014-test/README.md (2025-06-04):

# SiPM power regulator test board

This is a test board to provide the following features.  It is
intended to take as input ~65V bulk power from BZ's boost converter.

The final version would be stripped down to minimal parts and small
package sizes to fit on a future version of the detector adapter board.

* LT3014 high voltage regulator, programmable from 32-62V using a digital pot
* INA121 current sense / trip circuit.  Nominally set to trip at 10mA current but easy to change via resistor swap. 
* Set up (hopefully) to power up in a tripped state (HV off) until the R-Pi turns on the power
* Ability to measure output voltage and load current via R-Pi
* Socket for a Raspberry Pi Pico board for testing the interfaces.
* Testpoints and LEDs

## Revision History

* V1.0 - never fabricated
* V1.0a - as built with small changes suggested by BZ

## Debug log

### 2025-05-27
* Install Thonny on PC and micropython on the R-Pi.  Blinky working.
* Writing to the digital pot seems to work, but can't read back for some reason.

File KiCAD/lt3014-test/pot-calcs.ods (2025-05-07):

DPOT | R | R1 | R2 | VOUT
 | 5.00E+04 |  | 2.50E+06
5.00E+04 |  | 100000 |  | 31.7
2.50E+04 |  | 75000 |  | 41.9
1.00E+04 |  | 60000 |  | 52.1
5.00E+03 |  | 55000 |  | 56.7
0 |  | 50000 |  | 62.2

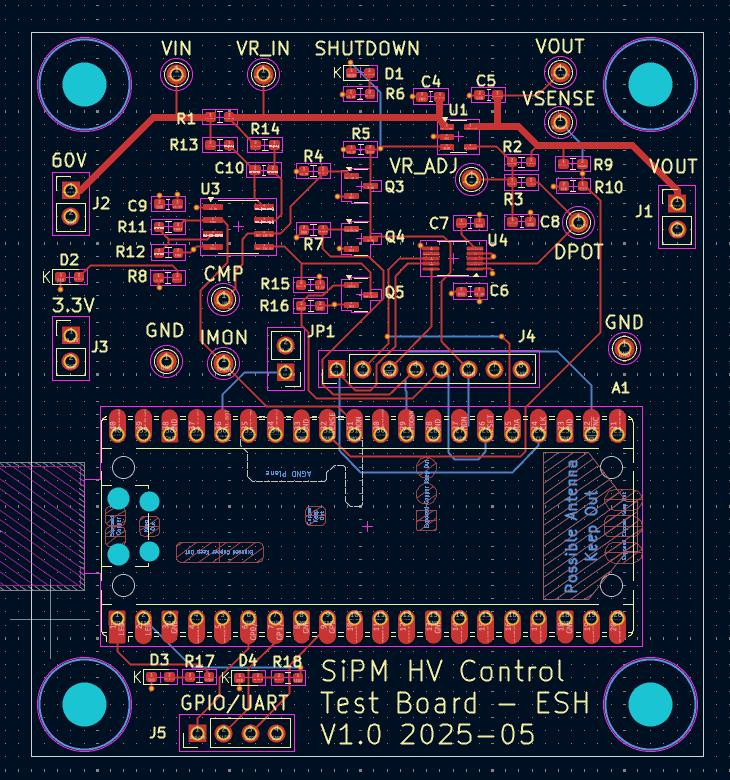
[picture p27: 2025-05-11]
KiCAD/lt3014-test/docs/Screenshot_2025-05-09_13-31-47.jpg

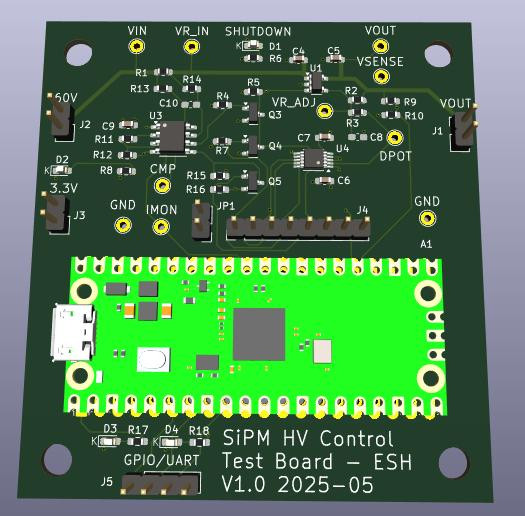
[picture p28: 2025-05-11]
KiCAD/lt3014-test/docs/pcb_3d.jpg

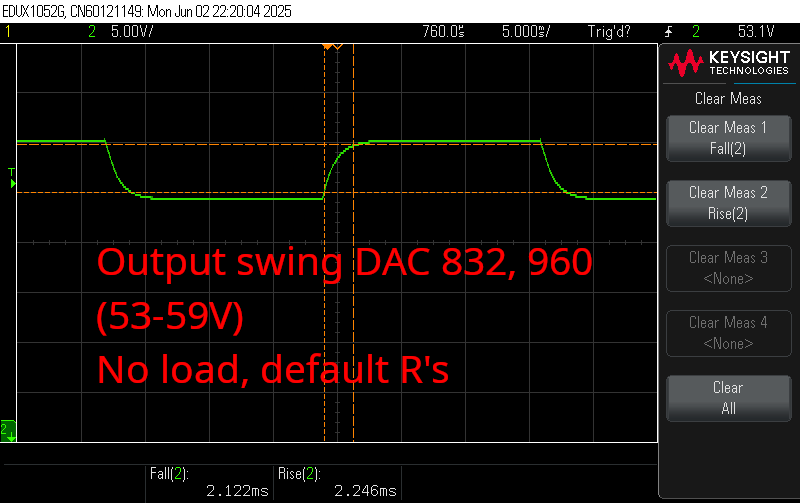
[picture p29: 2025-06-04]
Testing/LT3014/no_load.png

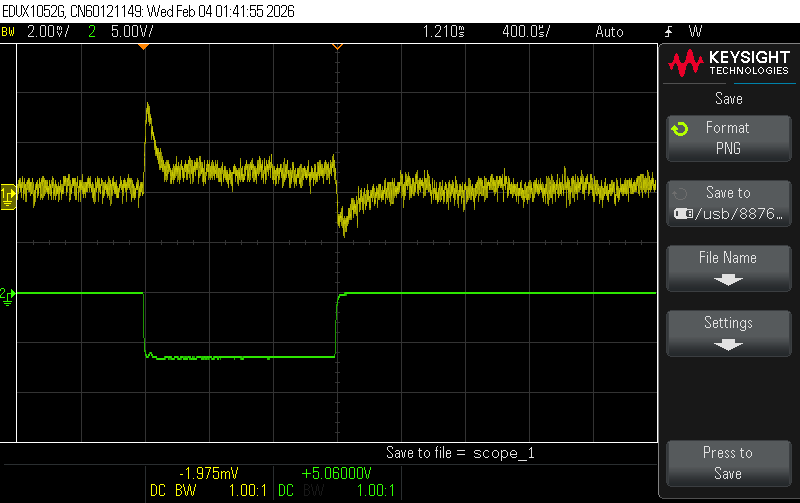
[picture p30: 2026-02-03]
Testing/sipm-splitter/scope_1.png

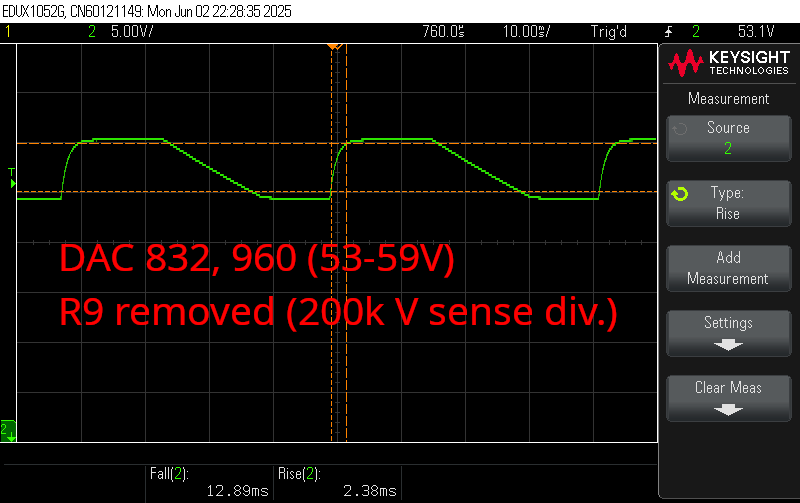
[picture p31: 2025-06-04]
Testing/LT3014/r9_out.png

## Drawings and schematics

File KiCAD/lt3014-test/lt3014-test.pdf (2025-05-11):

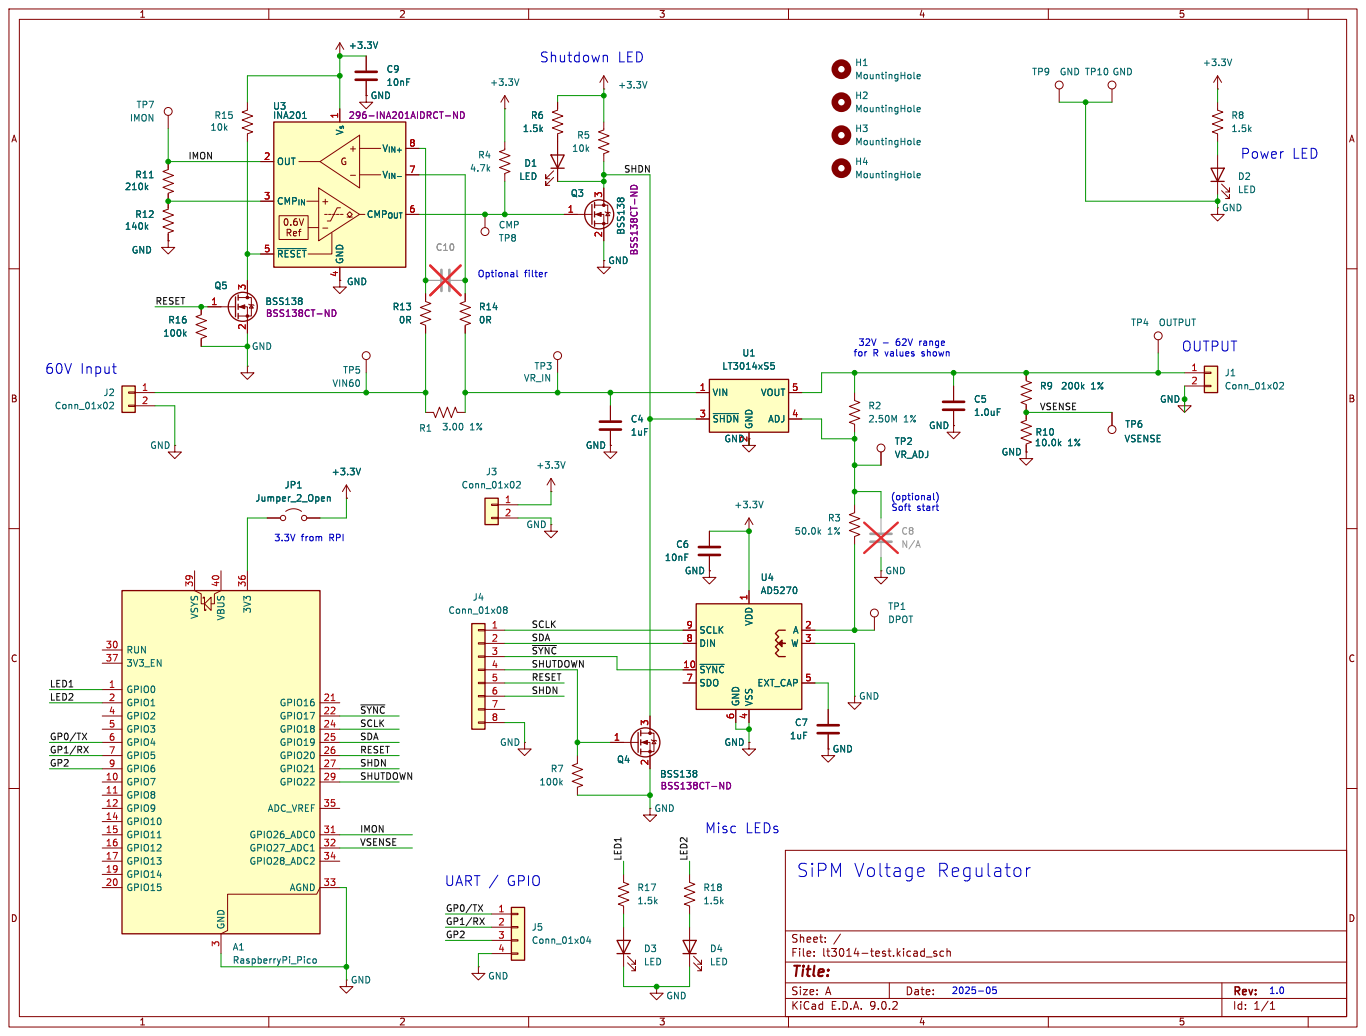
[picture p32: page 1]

4 V_{IN+}8 V_{IN-}7 CMP_{OUT} 6 GND

2 VOUT 5 ADJ 4 GND GND

(optional) Soft start Misc LEDs

Id: 1/1 Title: File: lt3014-test.kicad_sch Sheet: /

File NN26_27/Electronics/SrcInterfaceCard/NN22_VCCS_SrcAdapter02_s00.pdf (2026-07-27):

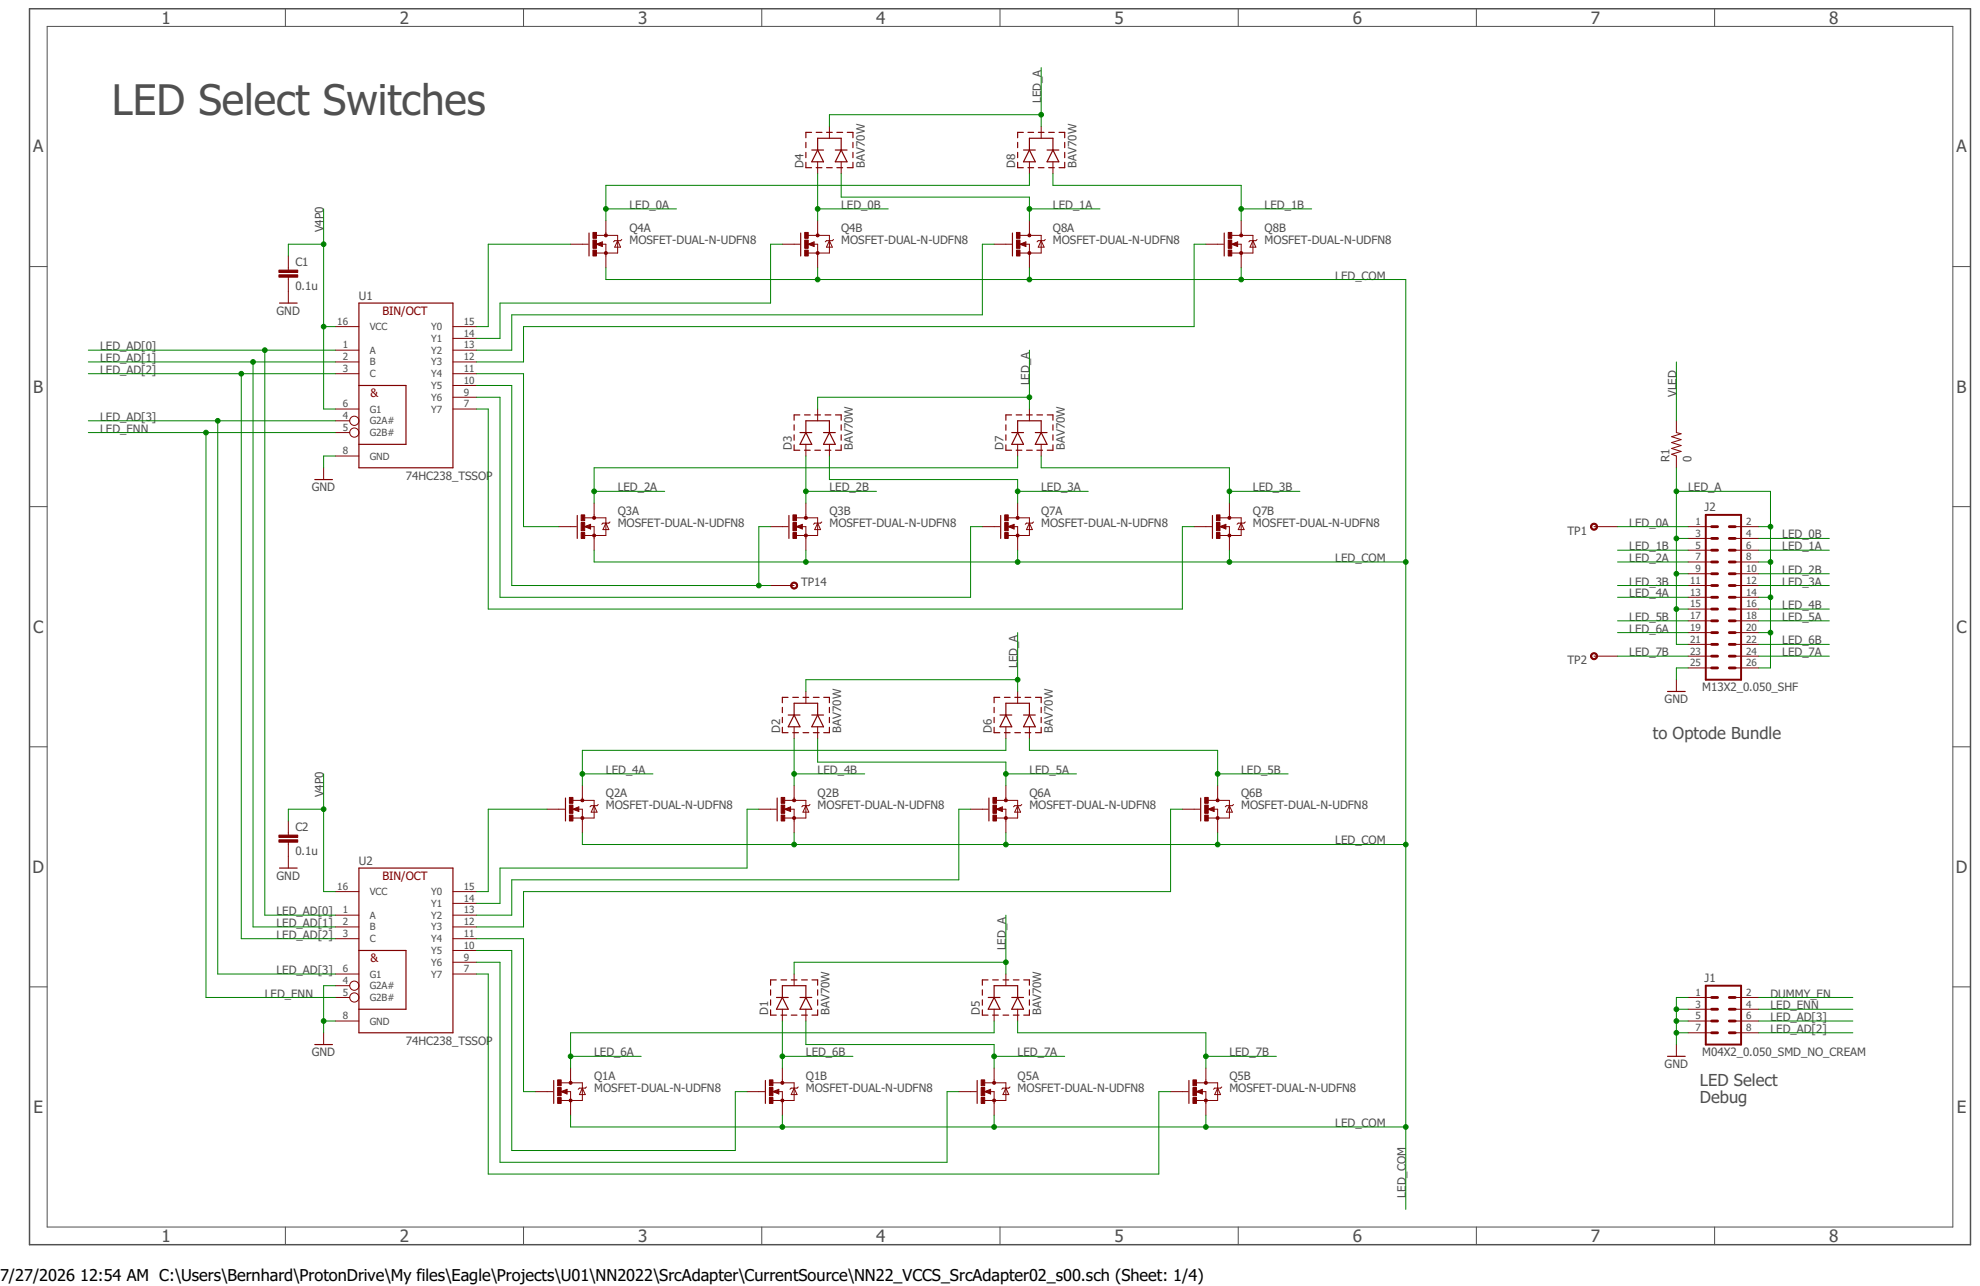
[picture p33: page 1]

7/27/2026 12:54 AM C:\Users\Bernhard\ProtonDrive\My files\Eagle\Projects\U01\NN2022\SrcAdapter\CurrentSource\NN22_VCCS_SrcAdapter02_s00.sch (Sheet: 1/4)

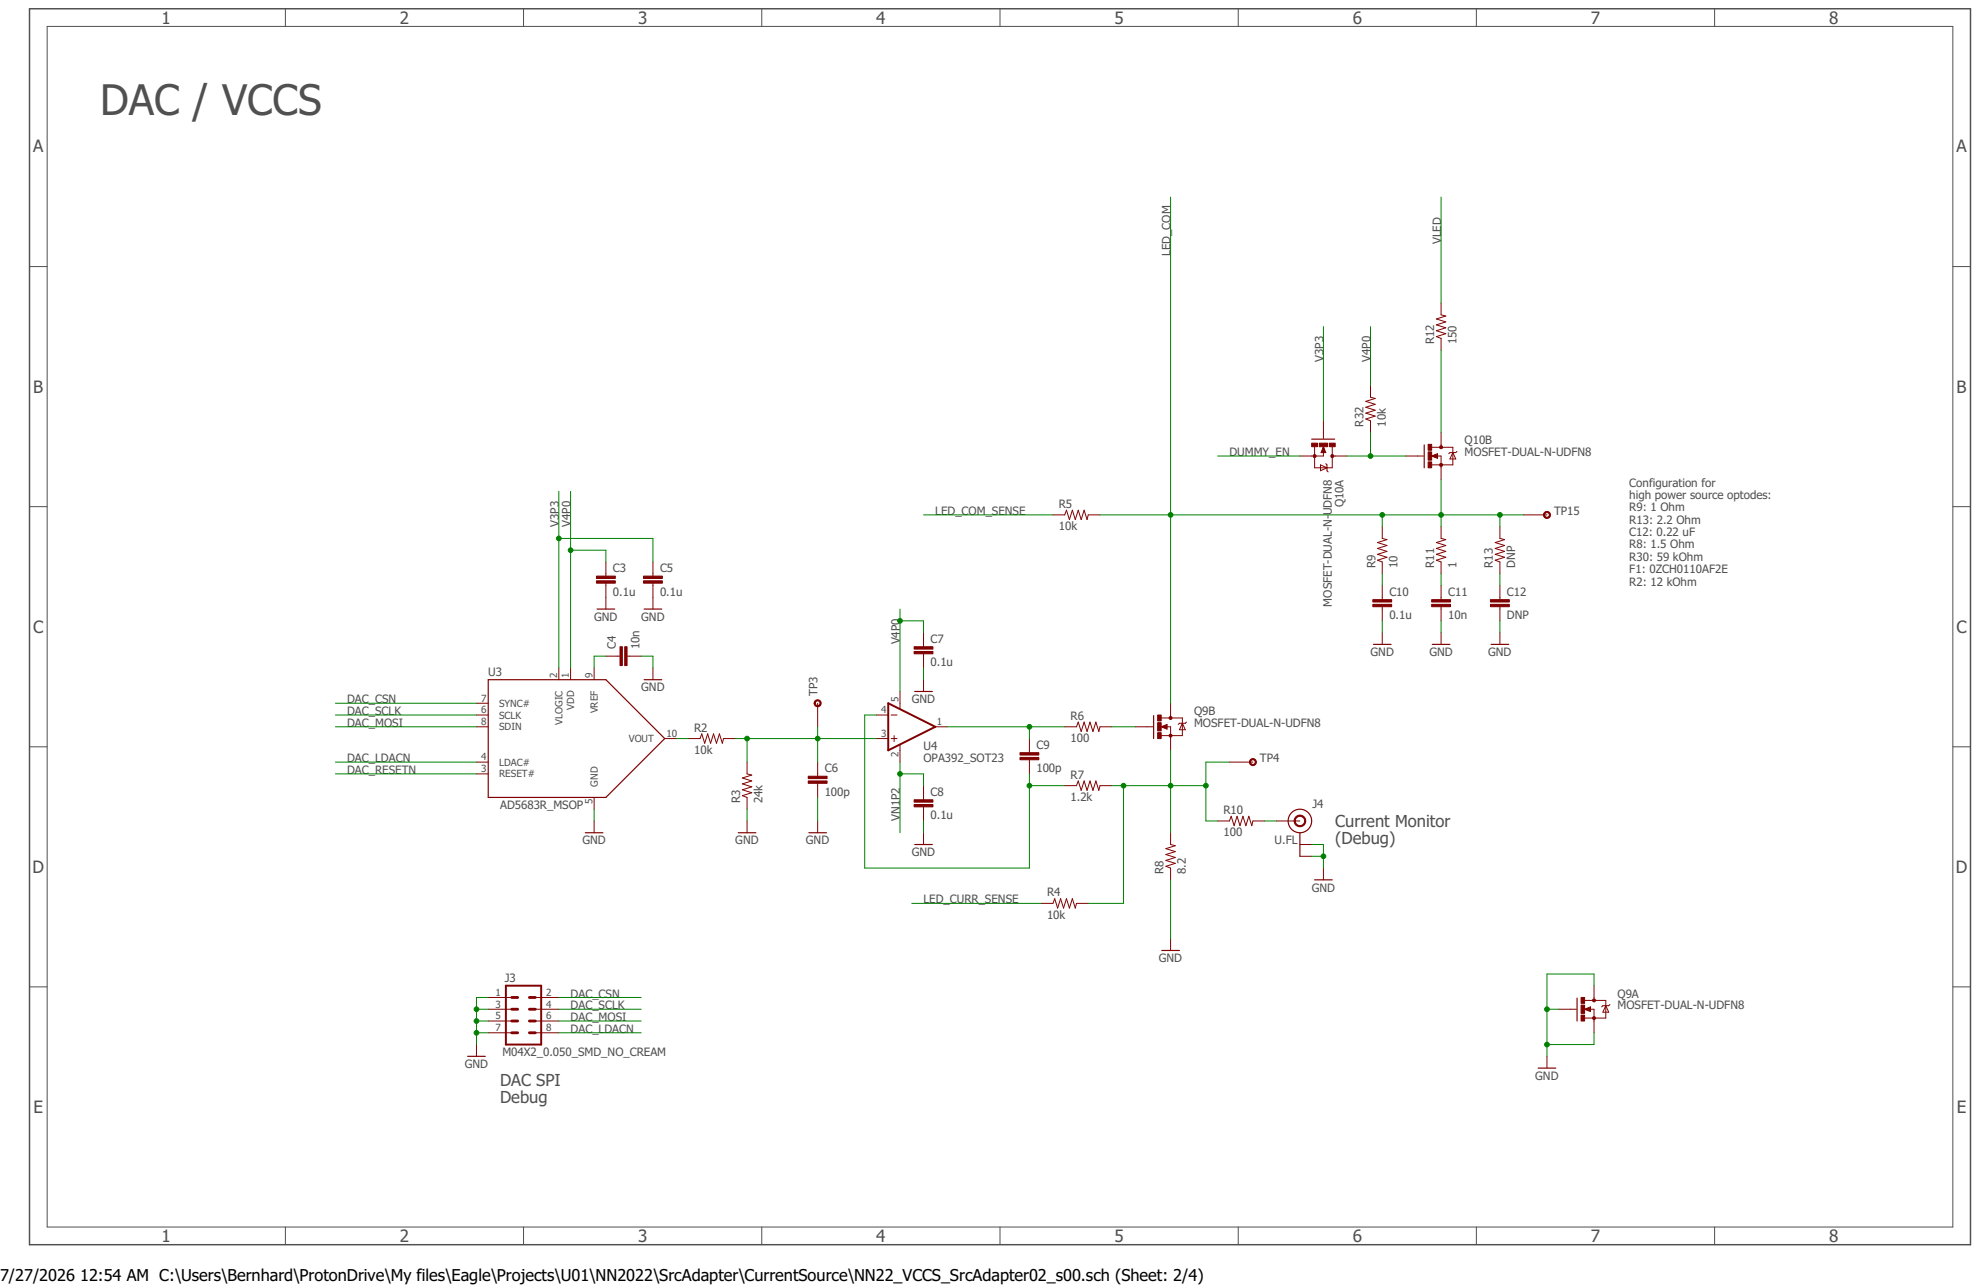
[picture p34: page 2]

Configuration for high power source optodes: R9: 1 Ohm

7/27/2026 12:54 AM C:\Users\Bernhard\ProtonDrive\My files\Eagle\Projects\U01\NN2022\SrcAdapter\CurrentSource\NN22_VCCS_SrcAdapter02_s00.sch (Sheet: 2/4)

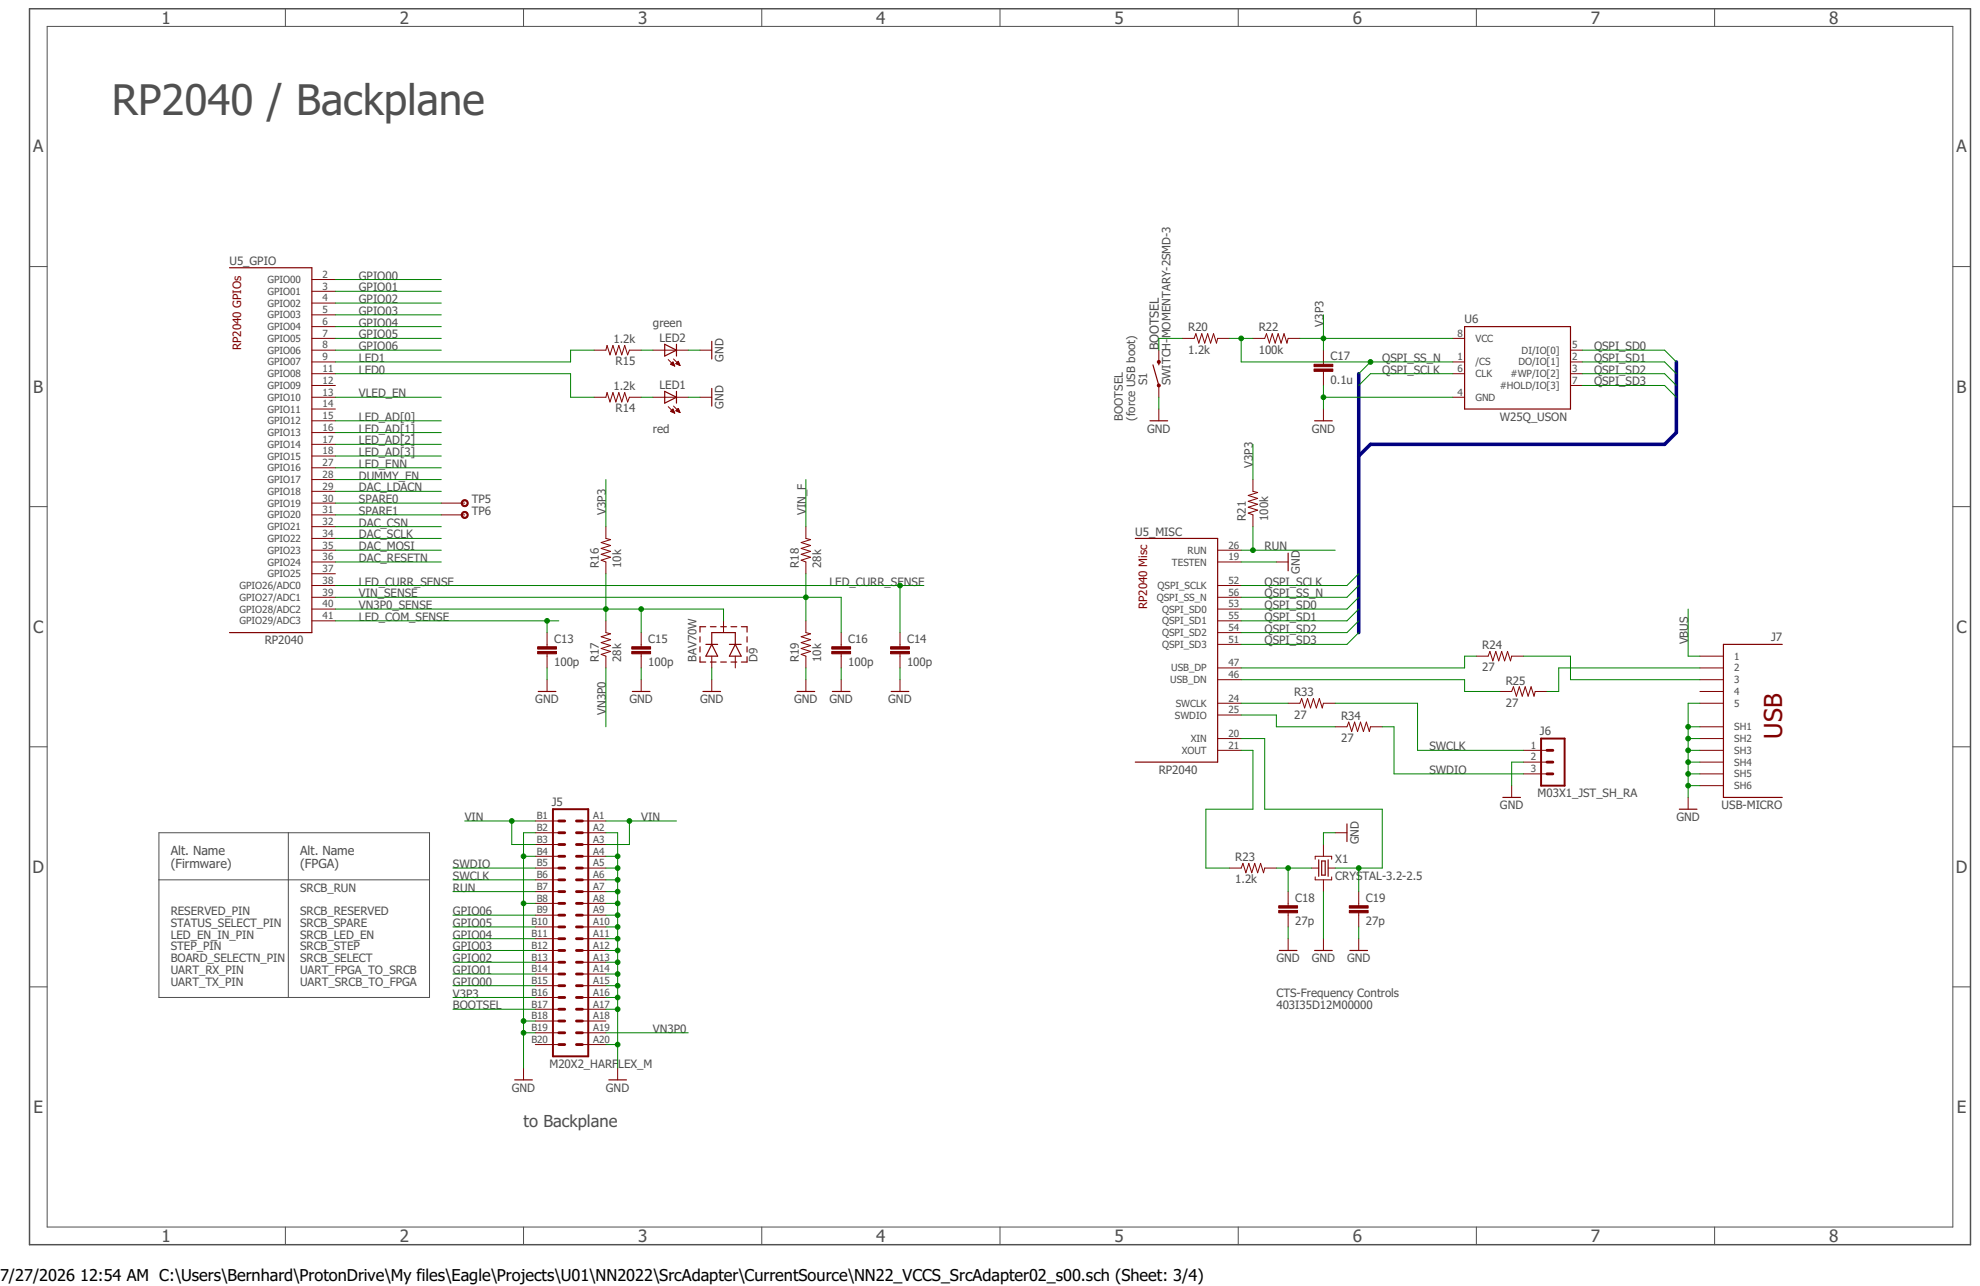
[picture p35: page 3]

Alt. Name (Firmware) | Alt. Name (FPGA)

RESERVED_PIN STATUS_SELECT_PIN LED_EN_IN_PIN STEP_PIN BOARD_SELECTN_PIN UART_RX_PIN UART_TX_PIN | SRCB_RUN SRCB_RESERVED SRCB_SPARE SRCB_LED_EN SRCB_STEP SRCB_SELECT UART_FPGA_TO_SRCB UART_SRCB_TO_FPGA

7/27/2026 12:54 AM C:\Users\Bernhard\ProtonDrive\My files\Eagle\Projects\U01\NN2022\SrcAdapter\CurrentSource\NN22_VCCS_SrcAdapter02_s00.sch (Sheet: 3/4)

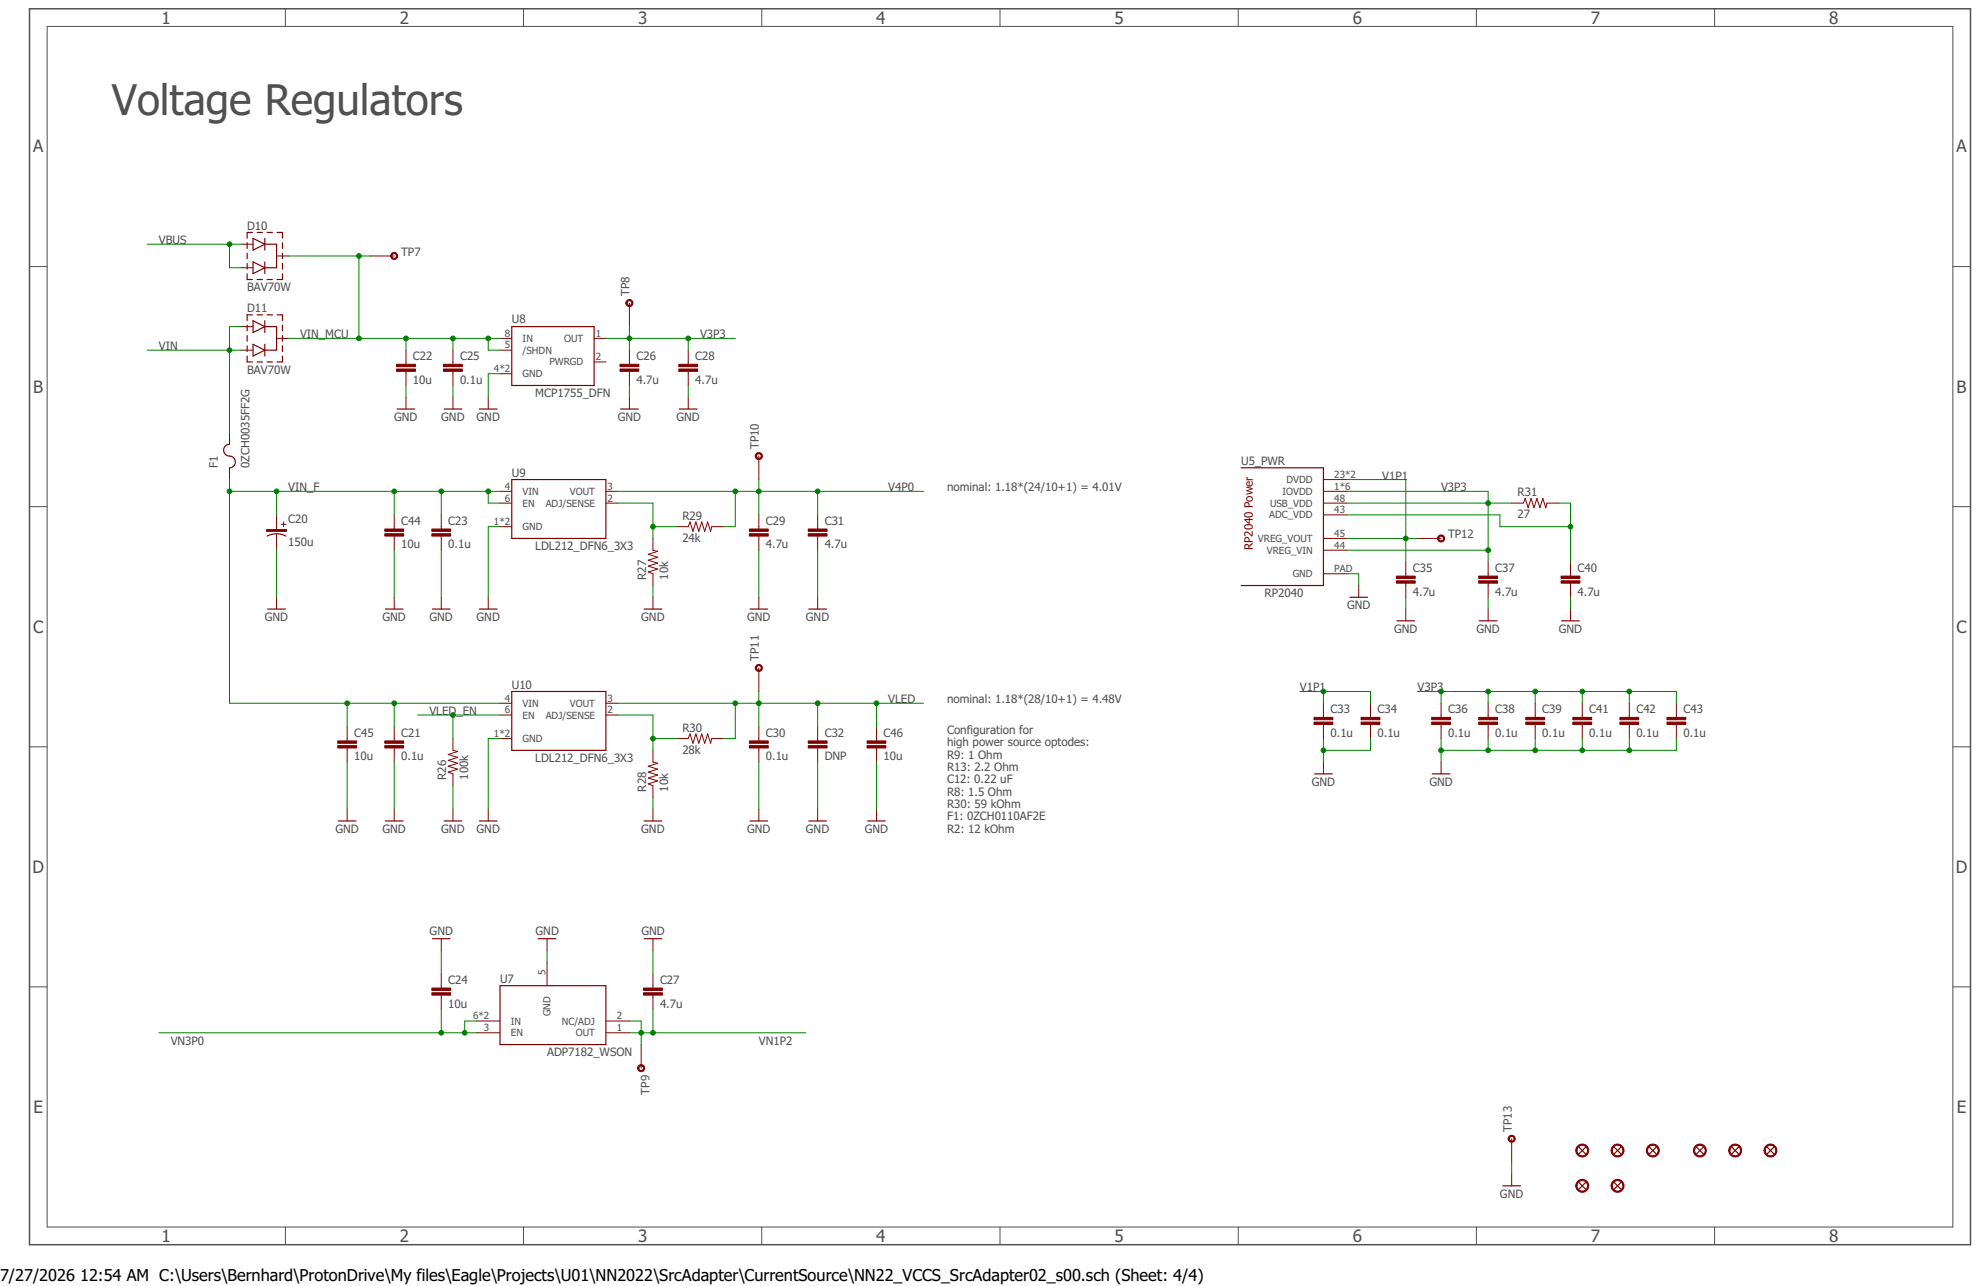
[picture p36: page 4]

Configuration for high power source optodes: R9: 1 Ohm

7/27/2026 12:54 AM C:\Users\Bernhard\ProtonDrive\My files\Eagle\Projects\U01\NN2022\SrcAdapter\CurrentSource\NN22_VCCS_SrcAdapter02_s00.sch (Sheet: 4/4)

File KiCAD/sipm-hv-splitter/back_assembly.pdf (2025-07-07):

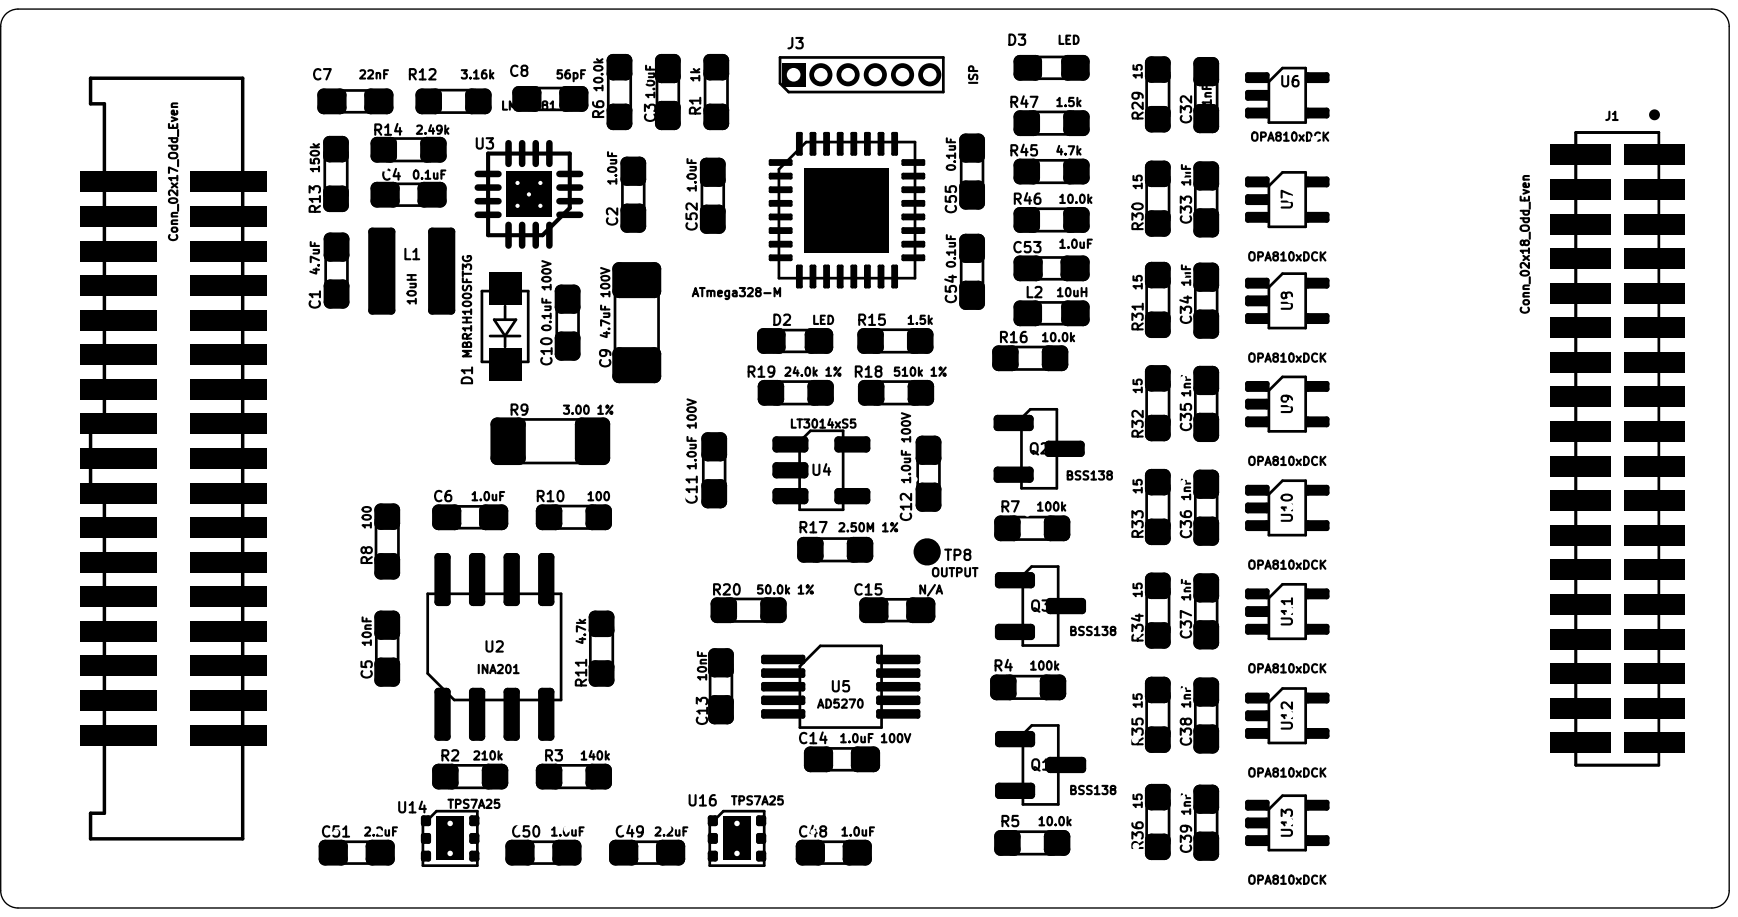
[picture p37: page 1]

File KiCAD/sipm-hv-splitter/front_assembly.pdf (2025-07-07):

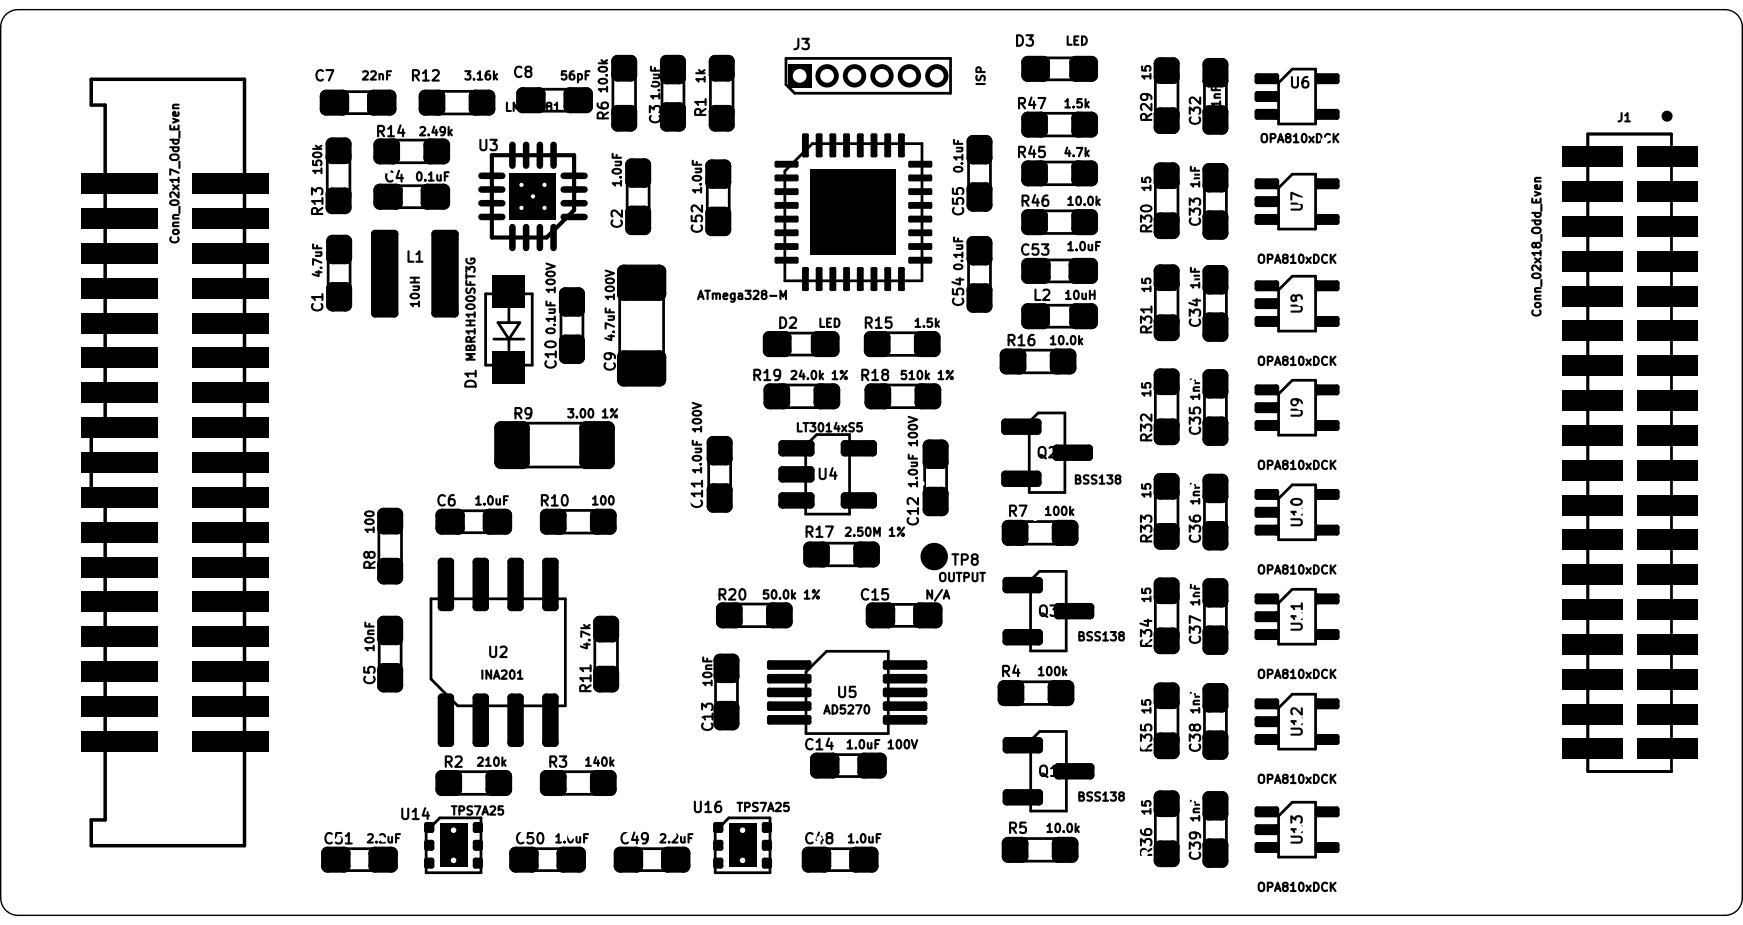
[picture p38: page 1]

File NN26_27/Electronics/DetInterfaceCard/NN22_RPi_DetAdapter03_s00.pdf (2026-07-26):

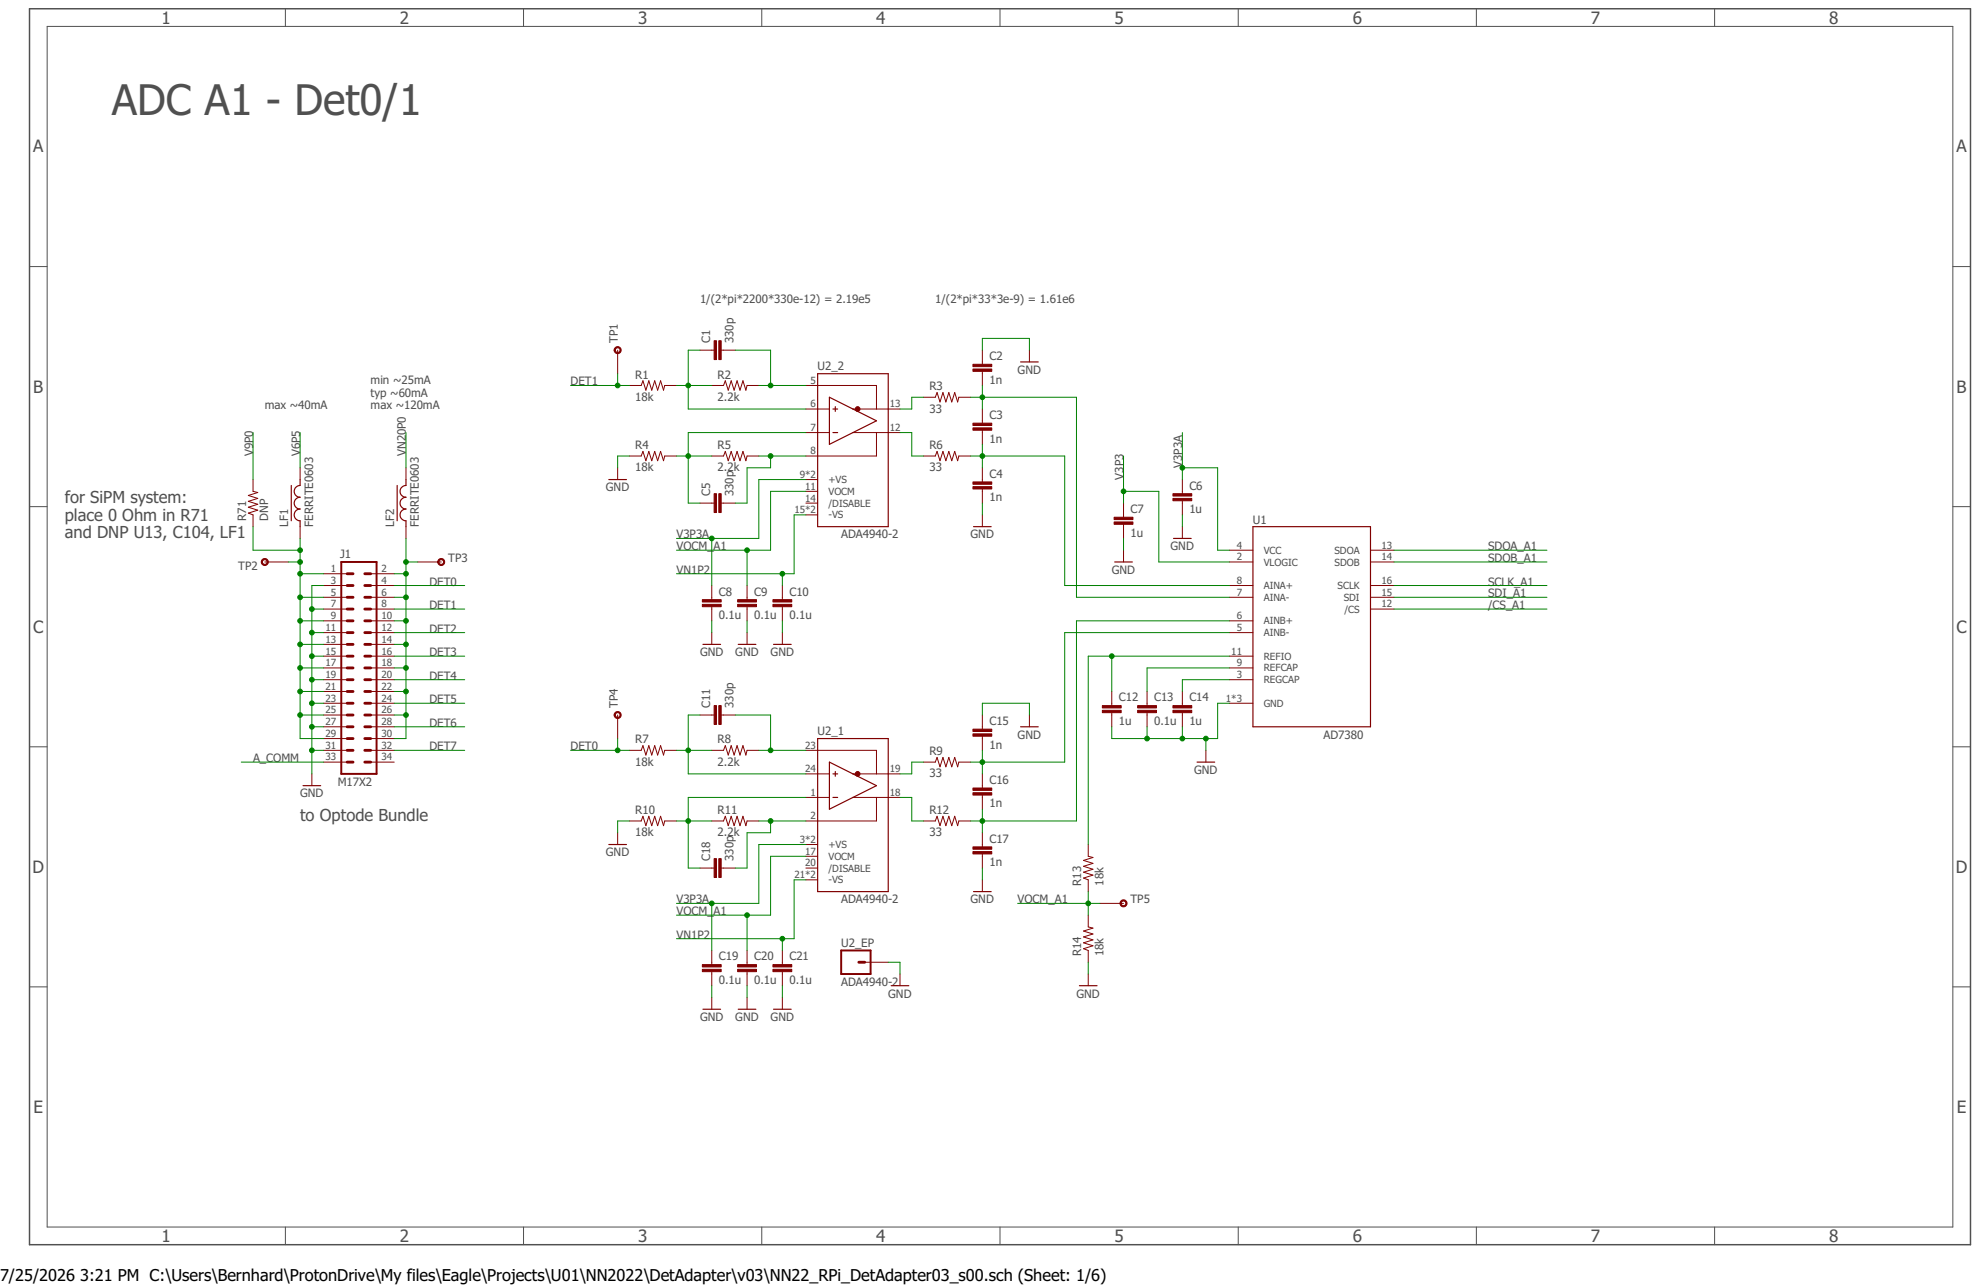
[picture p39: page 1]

VOCM /DISABLE -VS

7/25/2026 3:21 PM C:\Users\Bernhard\ProtonDrive\My files\Eagle\Projects\U01\NN2022\DetAdapter\v03\NN22_RPi_DetAdapter03_s00.sch (Sheet: 1/6)

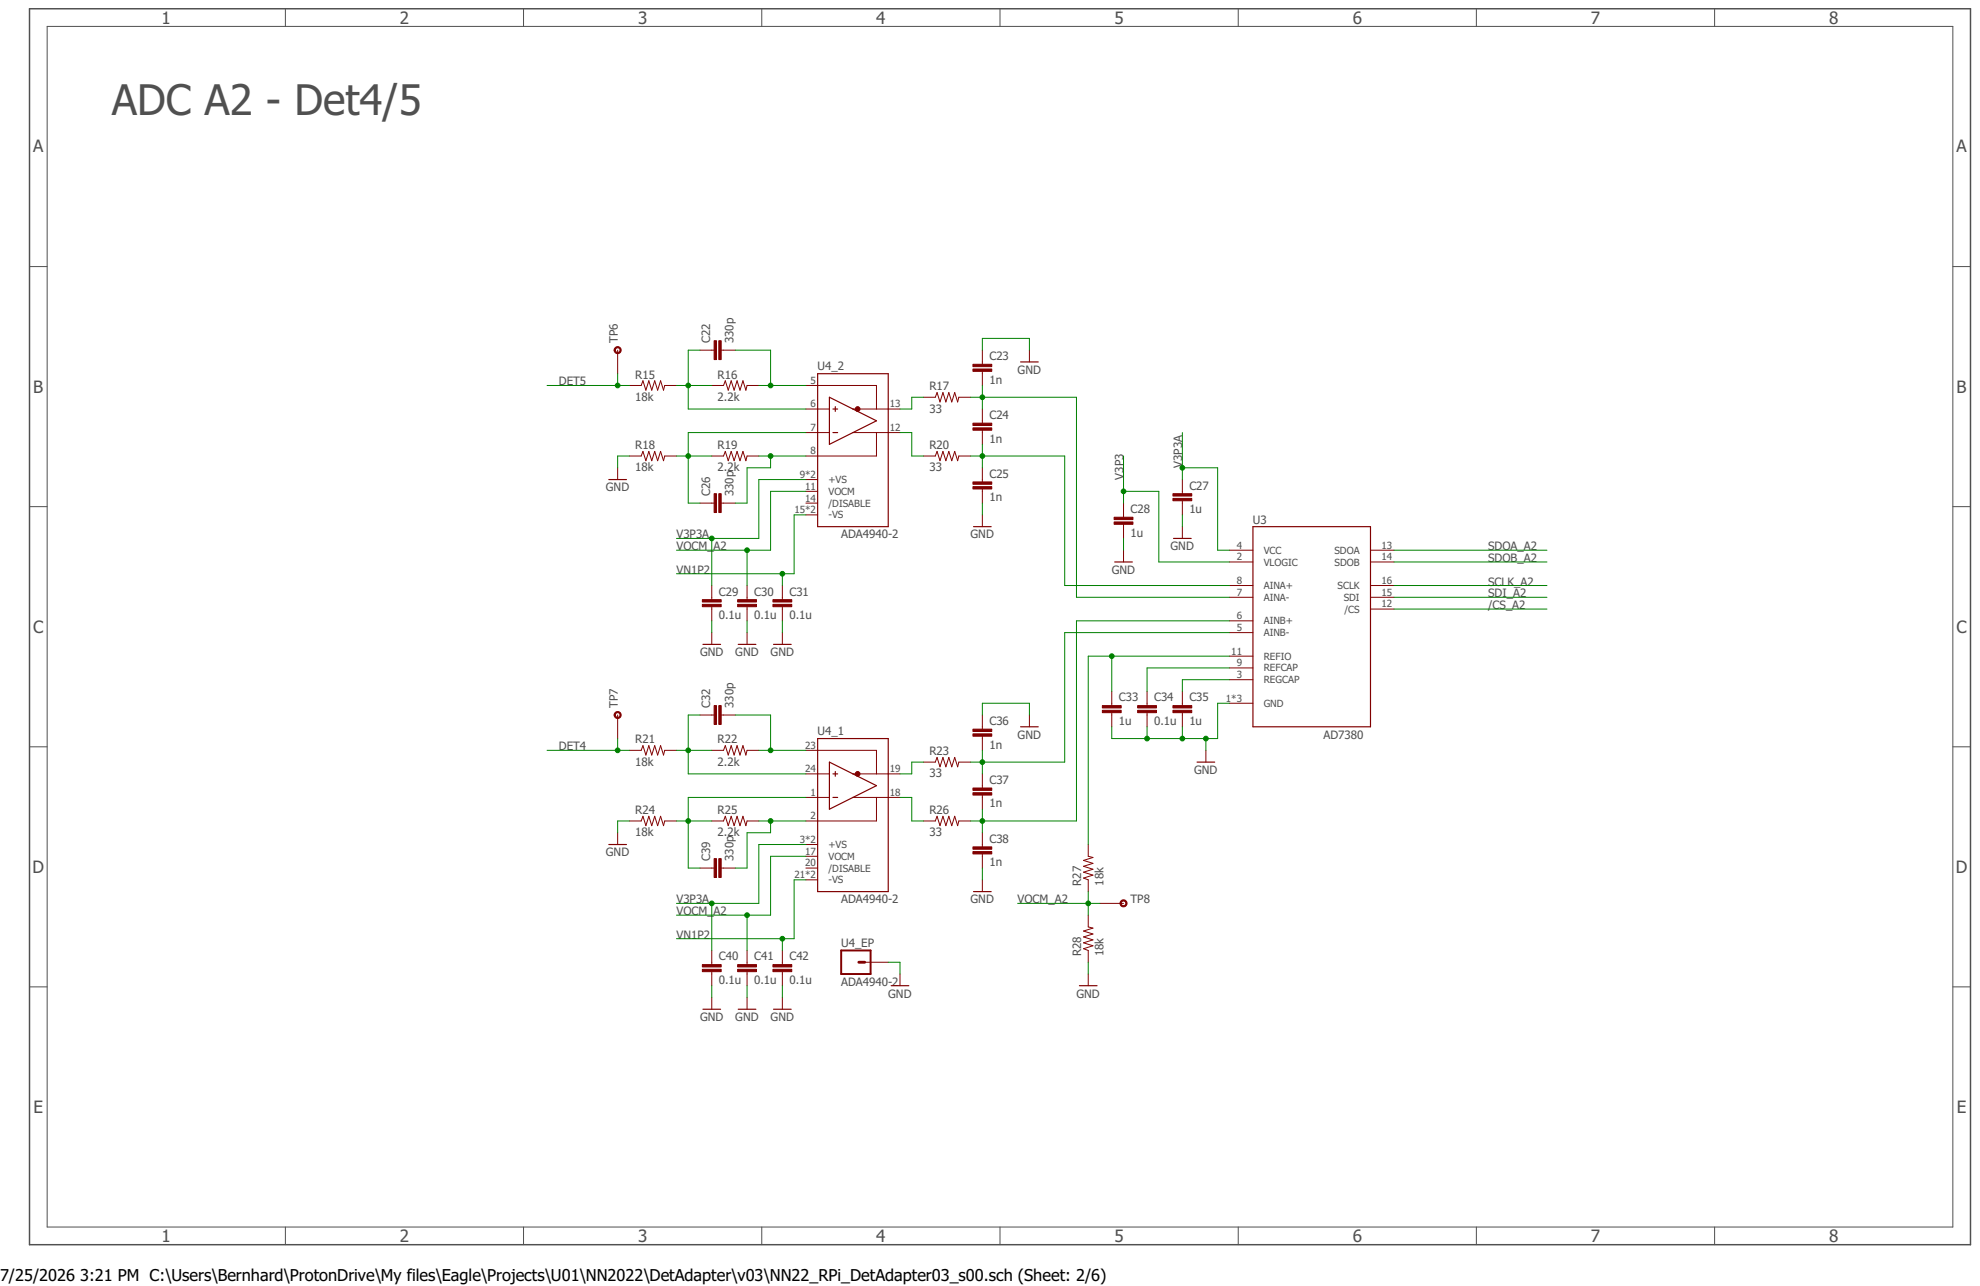
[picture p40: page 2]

VOCM /DISABLE -VS

7/25/2026 3:21 PM C:\Users\Bernhard\ProtonDrive\My files\Eagle\Projects\U01\NN2022\DetAdapter\v03\NN22_RPi_DetAdapter03_s00.sch (Sheet: 2/6)

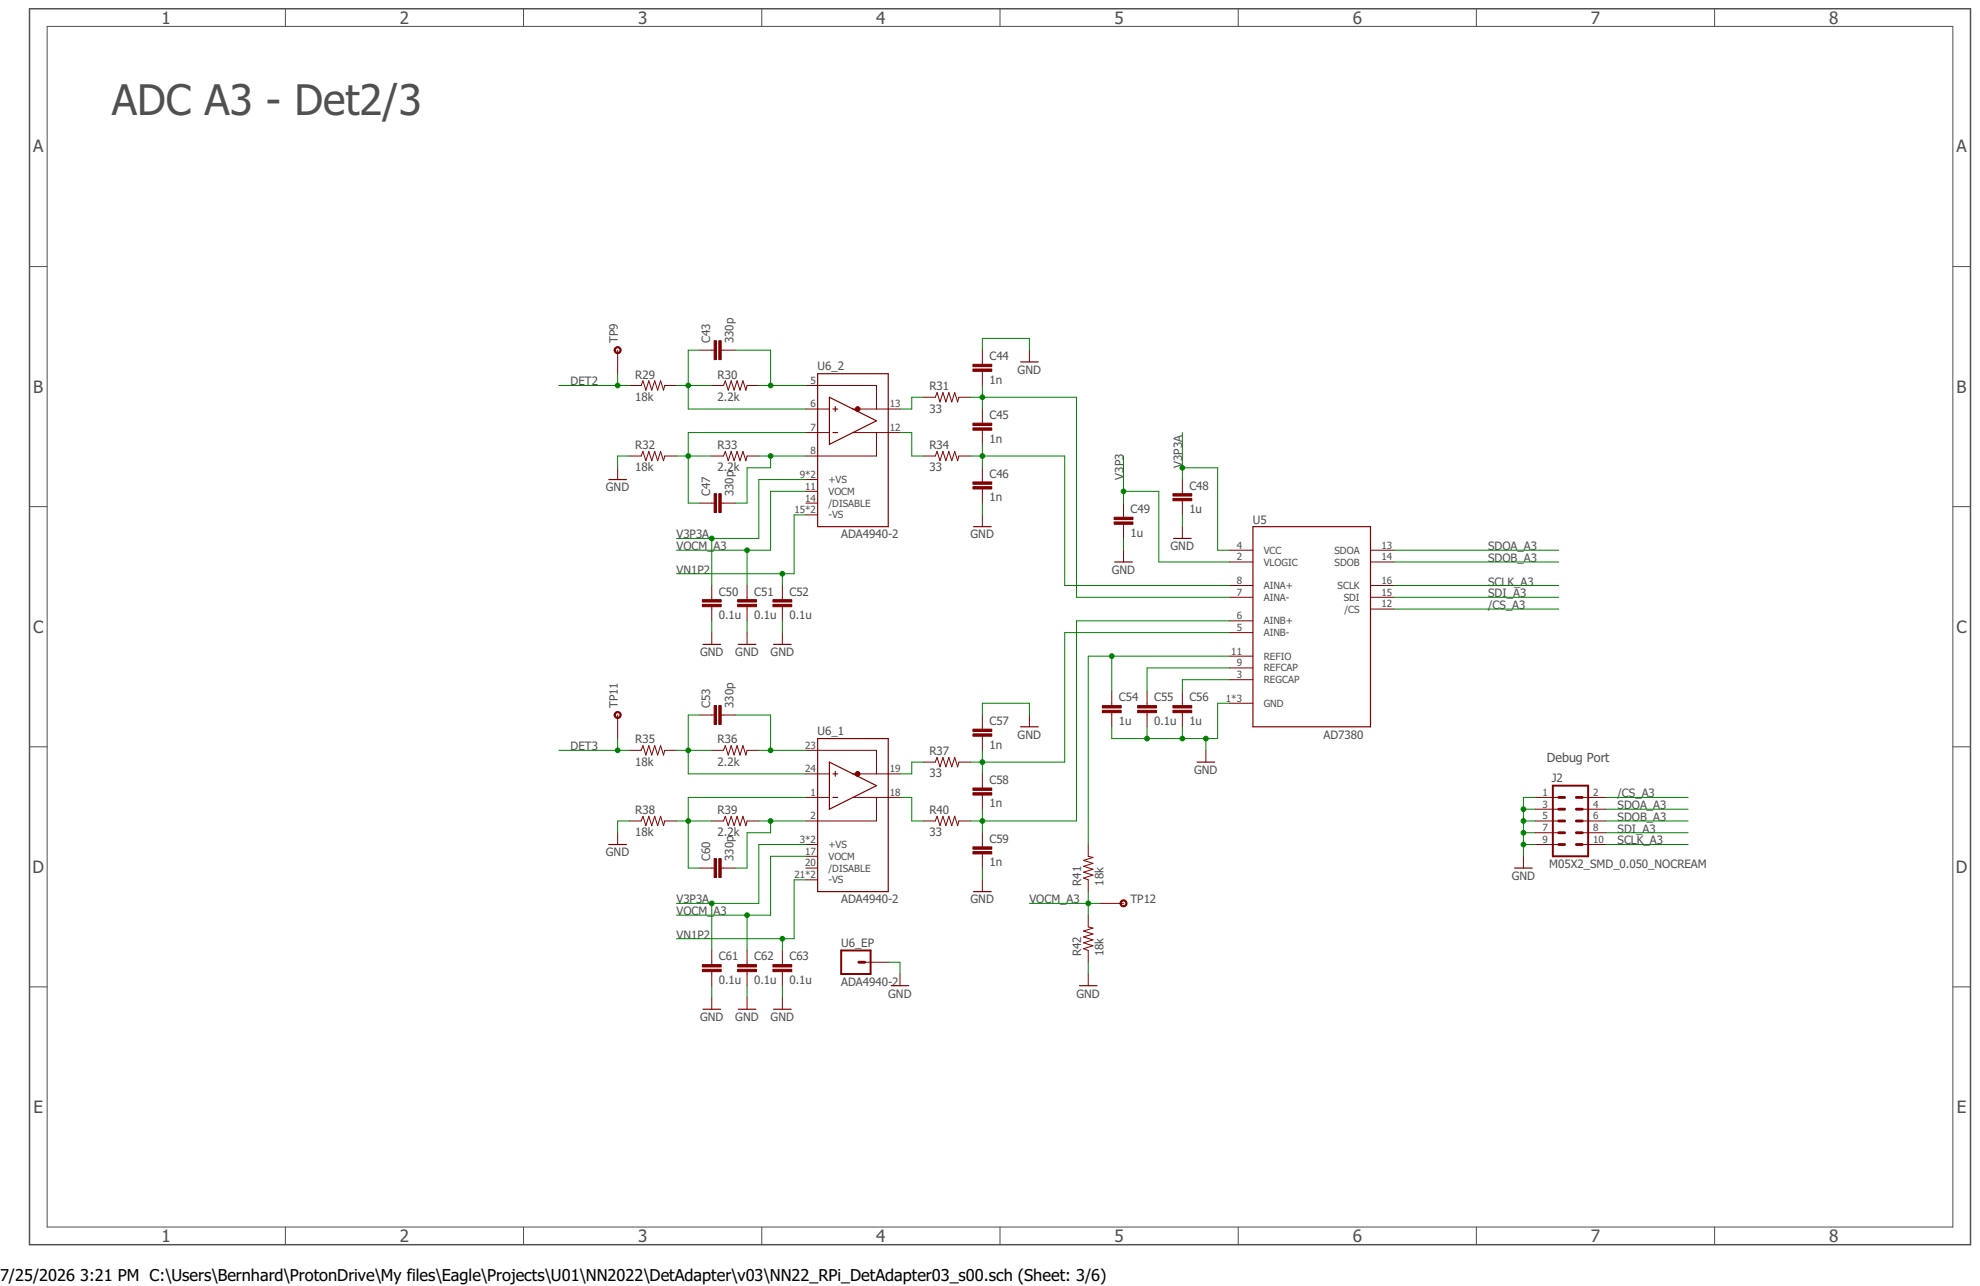
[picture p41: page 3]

VOCM /DISABLE -VS

7/25/2026 3:21 PM C:\Users\Bernhard\ProtonDrive\My files\Eagle\Projects\U01\NN2022\DetAdapter\v03\NN22_RPi_DetAdapter03_s00.sch (Sheet: 3/6)

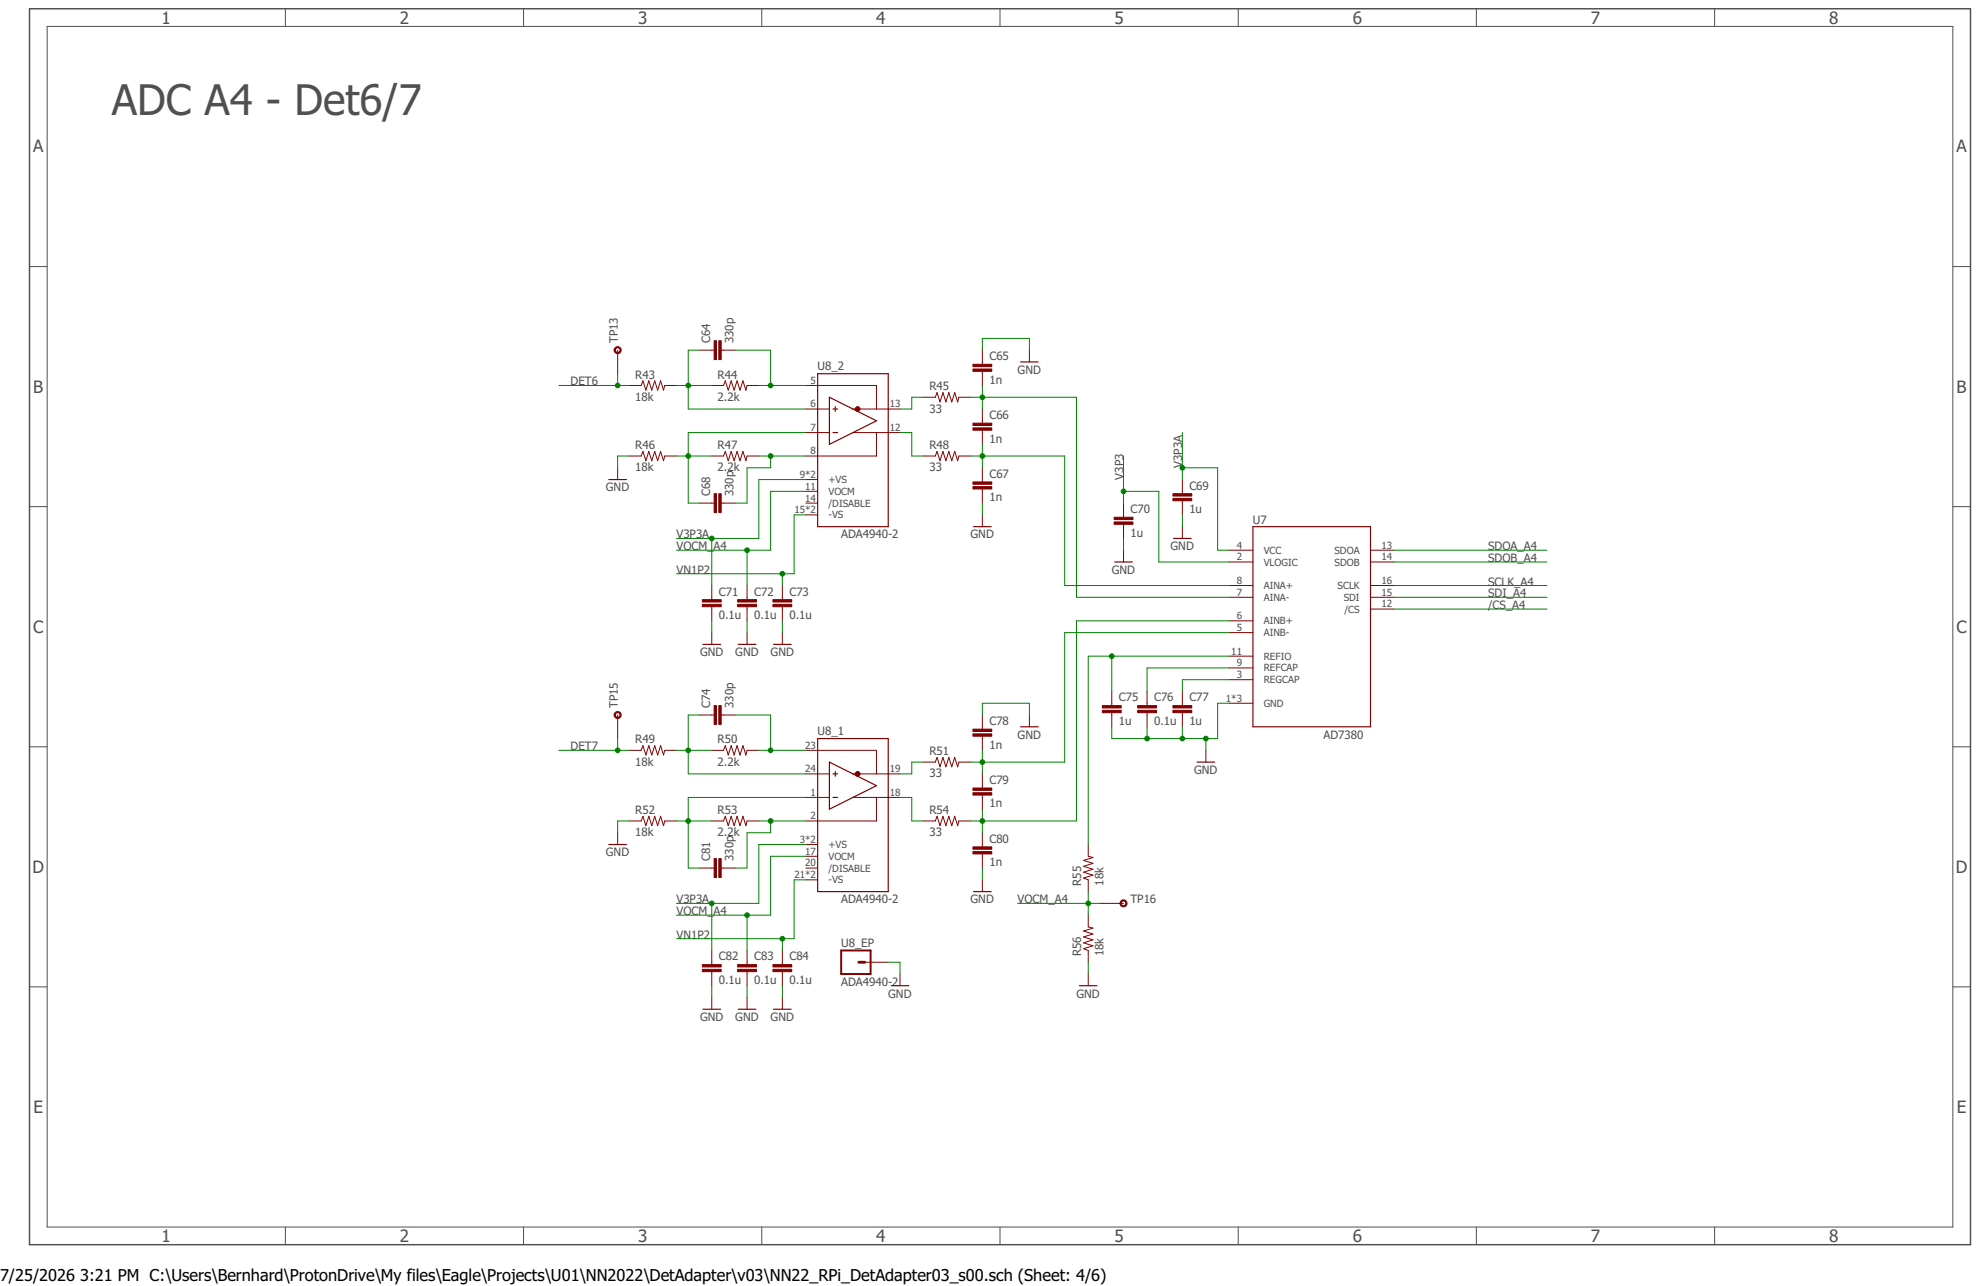
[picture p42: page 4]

VOCM /DISABLE -VS

7/25/2026 3:21 PM C:\Users\Bernhard\ProtonDrive\My files\Eagle\Projects\U01\NN2022\DetAdapter\v03\NN22_RPi_DetAdapter03_s00.sch (Sheet: 4/6)

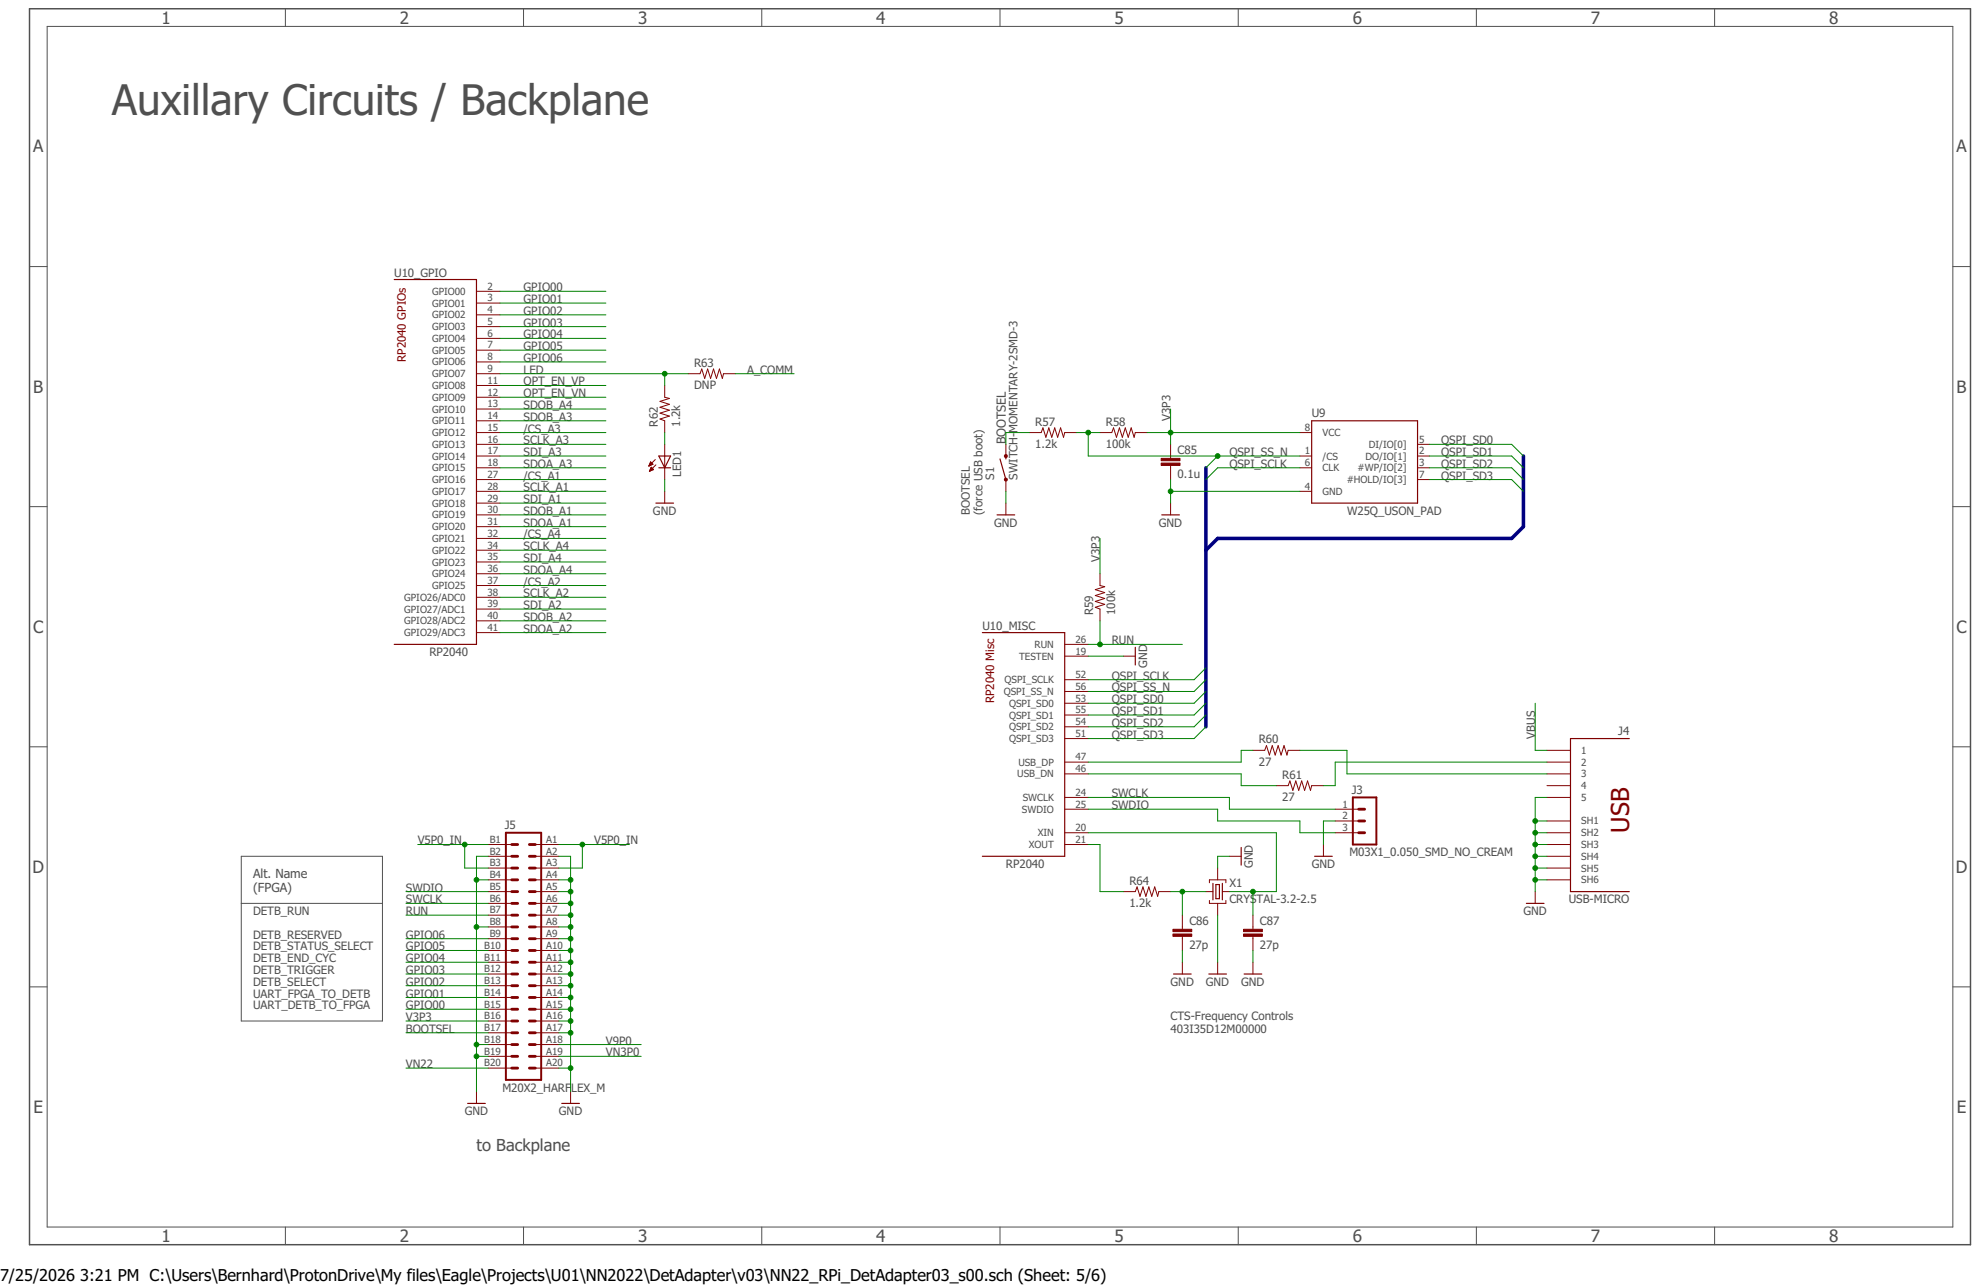
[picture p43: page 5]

7/25/2026 3:21 PM C:\Users\Bernhard\ProtonDrive\My files\Eagle\Projects\U01\NN2022\DetAdapter\v03\NN22_RPi_DetAdapter03_s00.sch (Sheet: 5/6)


48 ADC_VDD
43 VREG_VOUT 45 VREG_VIN | TP21

use 5V fixed output version
ADP7142ACPZN5.0-R7

7/25/2026 3:21 PM C:\Users\Bernhard\ProtonDrive\My files\Eagle\Projects\U01\NN2022\DetAdapter\v03\NN22_RPi_DetAdapter03_s00.sch (Sheet: 6/6)

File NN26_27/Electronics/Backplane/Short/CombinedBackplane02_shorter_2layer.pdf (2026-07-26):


Two Layer Source Adapter Backplane

VCCS Source Card compatible

7/25/2026 1:56 PM D:\ProtonDrive\My files\Eagle\Projects\U01\NN2022\Backplane\SourceBackplane\CombinedBackplane02_shorter_2layer.sch (Sheet: 1/4)


Two Layer Detector Adapter Backplane

Alt. Name (FPGA) | Alt. Name (RP2040)

DETB_RUN DETB_RESERVED DETB_STATUS_SELECT DETB_END_CYC DETB_TRIGGER DETB_SELECT UART_FPGA_TO_DETB UART_DETB_TO_FPGA | GPIO06 GPIO05 GPIO04 GPIO03 GPIO02 GPIO01 GPIO00

7/25/2026 1:56 PM D:\ProtonDrive\My files\Eagle\Projects\U01\NN2022\Backplane\SourceBackplane\CombinedBackplane02_shorter_2layer.sch (Sheet: 2/4)


Two Layer Detector Adapter Backplane

Alt. Name (FPGA) | Alt. Name (RP2040)

DETB_RUN DETB_RESERVED DETB_STATUS_SELECT DETB_END_CYC DETB_TRIGGER DETB_SELECT UART_FPGA_TO_DETB UART_DETB_TO_FPGA | GPIO06 GPIO05 GPIO04 GPIO03 GPIO02 GPIO01 GPIO00

7/25/2026 1:56 PM D:\ProtonDrive\My files\Eagle\Projects\U01\NN2022\Backplane\SourceBackplane\CombinedBackplane02_shorter_2layer.sch (Sheet: 3/4)


Two Layer Detector Adapter Backplane

Alt. Name (FPGA) | Alt. Name (RP2040)

DETB_RUN DETB_RESERVED DETB_STATUS_SELECT DETB_END_CYC DETB_TRIGGER DETB_SELECT UART_FPGA_TO_DETB UART_DETB_TO_FPGA | GPIO06 GPIO05 GPIO04 GPIO03 GPIO02 GPIO01 GPIO00

7/25/2026 1:56 PM D:\ProtonDrive\My files\Eagle\Projects\U01\NN2022\Backplane\SourceBackplane\CombinedBackplane02_shorter_2layer.sch (Sheet: 4/4)

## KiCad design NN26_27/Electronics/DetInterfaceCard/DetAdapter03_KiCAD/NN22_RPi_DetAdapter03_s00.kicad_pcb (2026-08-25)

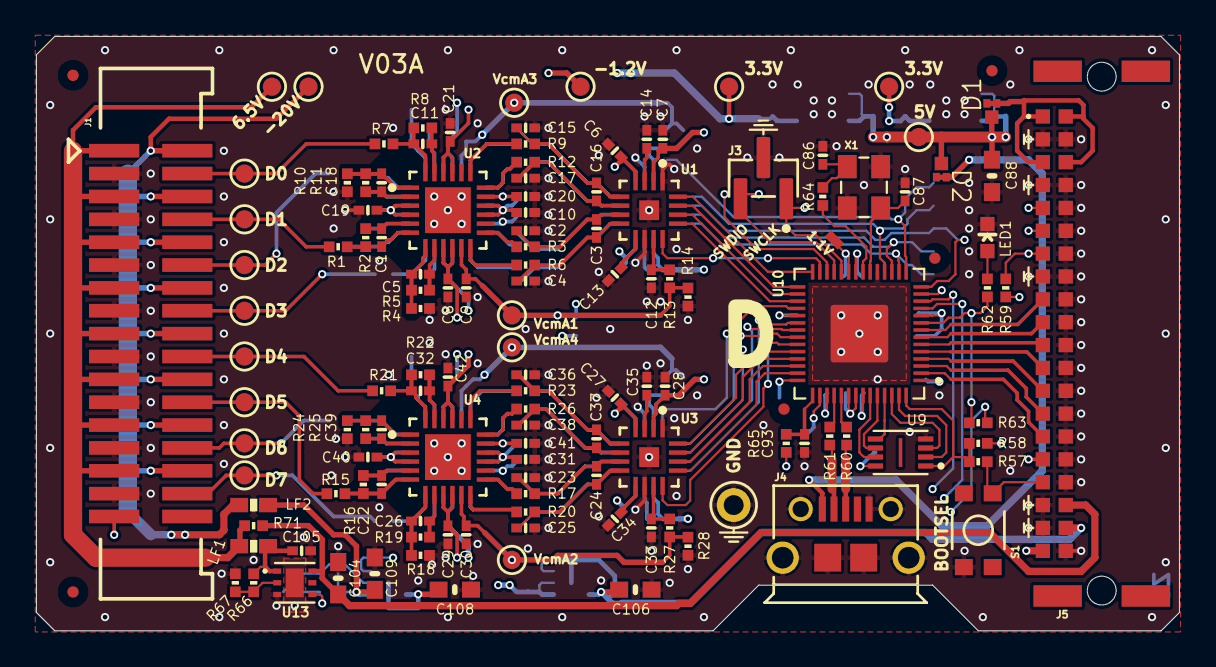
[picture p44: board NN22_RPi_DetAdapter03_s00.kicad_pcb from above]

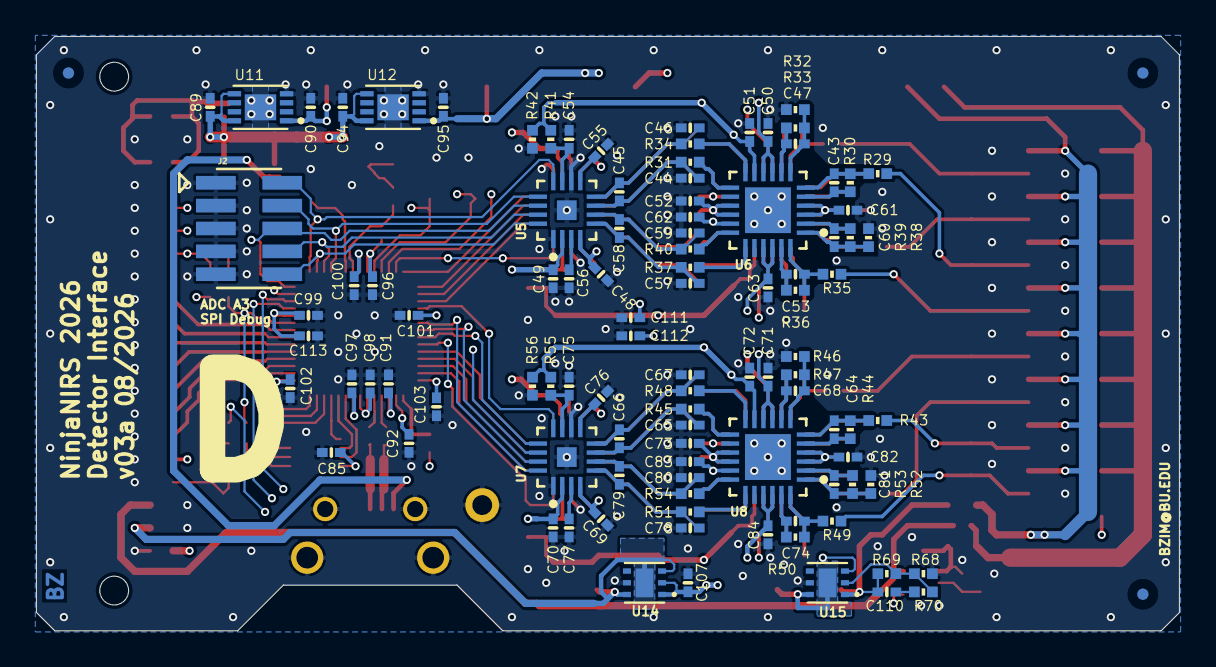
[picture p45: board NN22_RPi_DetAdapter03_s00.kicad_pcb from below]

Board: 6 copper layers, 63.5 x 33.0 mm, 239 parts (105 on the bottom side), 156 nets.

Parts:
C1, C5, C11, C18, C22, C26, C32, C39, C43, C47, C53, C60, C64, C68, C74, C81: 330p; 0402-CAP
C2, C3, C4, C15, C16, C17, C23, C24, C25, C36, C37, C38, C44, C45, C46, C57, C58, C59, C65, C66, C67, C78, C79, C80: 1n; 0402-CAP
C6, C7, C12, C14, C27, C28, C33, C35, C48, C49, C54, C56, C69, C70, C75, C77: 1u; 0402-CAP
C8, C9, C10, C13, C19, C20, C21, C29, C30, C31, C34, C40, C41, C42, C50, C51, C52, C55, C61, C62, C63, C71, C72, C73, C76, C82, C83, C84, C85, C96, C97, C98, C99, C100, C101, C102, C103: 0.1u; 0402-CAP
C86, C87: 27p; 0402-CAP
C88, C104, C106, C108, C109: 10u; 0603-CAP
C89, C90, C91, C92, C93, C94, C95, C105, C107, C111, C112, C113: 4.7u; 0402-CAP
C110: 33n; 0402-CAP
D1, D2: SBR1U40LP; DFN1411
FID1, FID2, FID3, FID4, FID5, FID6, FID7, FID8: FIDUCIALUFIDUCIAL; MICRO-FIDUCIAL
J1: M17X2; M17X2_0.050_SHF
J2: M05X2_SMD_0.050_NOCREAM; M05X2_0.050_SMD_NO_CREAM
J3: M03X1_0.050_SMD_NO_CREAM
J4: USB-MICRO
J5: M20X2_HARFLEX_M
LED1: LED0603; LED-0603
LF1, LF2: FERRITE0603; 0603-FER
R1, R4, R7, R10, R13, R14, R15, R18, R21, R24, R27, R28, R29, R32, R35, R38, R41, R42, R43, R46, R49, R52, R55, R56: 18k; 0402-RES
R2, R5, R8, R11, R16, R19, R22, R25, R30, R33, R36, R39, R44, R47, R50, R53: 2.2k; 0402-RES
R3, R6, R9, R12, R17, R20, R23, R26, R31, R34, R37, R40, R45, R48, R51, R54, R65: 33; 0402-RES
R57, R62, R64: 1.2k; 0402-RES
R58, R59, R67: 100k; 0402-RES
R60, R61: 27; 0402-RES
R63, R71: DNP; 0402-RES
R66: 30k; 0402-RES
R68, R70: 10k; 0402-RES
R69: 154k; 0402-RES
S1: SWITCH-MOMENTARY-2SMD-3; TACTILE_SWITCH_SMD-3
TP1, TP2, TP3, TP4, TP5, TP6, TP7, TP8, TP9, TP11, TP12, TP13, TP15, TP16, TP17, TP18, TP19, TP22: TESTPOINT_ROUND; TESTPAD_ROUND
TP20: TESTPOINT1X01; 1X01
TP21: TESTPOINTPADSMALL; TESTPAD_SMALL
U1, U3, U5, U7: AD7380; LFCSP16
U2, U4, U6, U8: ADA4940-2; LFCSP24
U9: W25Q_USON_PAD; USON8L-2X3MM_APM
U10: RP2040; QFN-56_EP
U11, U12: MCP1755_DFN; DFN8_2X3MM
U13: ADP7142_WSON; WSON6
U14, U15: ADP7182_WSON; WSON6
X1: CRYSTAL-3.2-2.5

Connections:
A_COMM: J1.33, R63.2
BOOTSEL: J5.B17 (33), R57.1, S1.4 (2)
DET0: J1.4, R7.1, TP4.P$1 (P$1_P$1)
DET1: J1.8, R1.1, TP1.P$1 (P$1_P$1)
DET2: J1.12, R29.1, TP9.P$1 (P$1_P$1)
DET3: J1.16, R35.1, TP11.P$1 (P$1_P$1)
DET4: J1.20, R21.1, TP7.P$1 (P$1_P$1)
DET5: J1.24, R15.1, TP6.P$1 (P$1_P$1)
DET6: J1.28, R43.1, TP13.P$1 (P$1_P$1)
DET7: J1.32, R49.1, TP15.P$1 (P$1_P$1)
GND: C2.1, C4.2, C6.2, C7.2, C8.2, C9.2, C10.2, C12.2, C13.2, C14.2, C15.1, C17.2, C19.2, C20.2, C21.2, C23.1, C25.2, C27.2, C28.2, C29.2, C30.2, C31.2, C33.2, C34.2, C35.2, C36.1, C38.2, C40.2, C41.2, C42.2, C44.1, C46.2, C48.2, C49.2, C50.2, C51.2, C52.2, C54.2, C55.2, C56.2, C57.1, C59.2, C61.2, C62.2, C63.2, C65.1, C67.2, C69.2, C70.2, C71.2, C72.2, C73.2, C75.2, C76.2, C77.2, C78.1, C80.2, C82.2, C83.2, C84.2, C85.2, C86.2, C87.2, C88.2, C89.2, C90.2, C91.2, C92.2, C93.2, C94.2, C95.2, C96.2, C97.2, C98.2, C99.2, C100.2, C101.2, C102.2, C103.2, C104.2, C105.2, C106.1, C107.1, C108.1, C109.1, C111.2, C112.1, C113.2, J1.3, J1.7, J1.11, J1.15, J1.19, J1.23, J1.27, J1.31, J2.1, J2.3, J2.5, J2.7, J2.9, J3.2, J4.5, J4.SH1, J4.SH2, J4.SH3, J4.SH4, J4.SH5, J4.SH6, J5.A2 (4), J5.A4 (8), J5.A5 (10), J5.A6 (12), J5.A7 (14), J5.A8 (16), J5.A9 (18), J5.A10 (20), J5.A11 (22), J5.A12 (24), J5.A13 (26), J5.A14 (28), J5.A15 (30), J5.A16 (32), J5.A17 (34), J5.A20 (40), J5.B2 (3), J5.B4 (7), J5.B8 (15), J5.B18 (35), J5.B19 (37), LED1.C, R4.1, R10.1, R14.1, R18.1, R24.1, R28.1, R32.1, R38.1, R42.1, R46.1, R52.1, R56.1, R67.1, R68.2, S1.1, TP20.1 (P$1_1), U1.1 (GND), U1.10 (GND), U1.EP (GND), U2.EP (1), U3.1 (GND), U3.10 (GND), U3.EP (GND), U4.EP (1), U5.1 (GND), U5.10 (GND), U5.EP (GND), U6.EP (1), U7.1 (GND), U7.10 (GND), U7.EP (GND), U8.EP (1), U9.4 (GND), U10.19 (TESTEN), U10.PAD (GND), U11.4 (GND), U11.P (GND), U12.4 (GND), U12.P (GND), U13.3 (GND), U13.PAD (GND), U14.5 (GND), U15.5 (GND), X1.2 (GND), X1.4 (GND)
GPIO00: J5.B15 (29), U10.2 (GPIO00)
GPIO01: J5.B14 (27), U10.3 (GPIO01)
GPIO02: J5.B13 (25), U10.4 (GPIO02)
GPIO03: J5.B12 (23), U10.5 (GPIO03)
GPIO04: J5.B11 (21), U10.6 (GPIO04)
GPIO05: J5.B10 (19), U10.7 (GPIO05)
GPIO06: J5.B9 (17), U10.8 (GPIO06)
LED: R62.2, R63.1, U10.9 (GPIO07)
unnamed: C110.1, R70.1
unnamed: J4.2, R61.2
unnamed: J4.3, R60.2
unnamed: LED1.A, R62.1
unnamed: J1.1, J1.5, J1.9, J1.13, J1.17, J1.21, J1.25, J1.29, LF1.1, R71.1, TP2.P$1 (P$1_P$1)
unnamed: J1.2, J1.6, J1.10, J1.14, J1.18, J1.22, J1.26, J1.30, LF2.1, TP3.P$1 (P$1_P$1)
unnamed: C3.2, C4.1, R6.2, U1.8 (AINA+)
unnamed: C2.2, C3.1, R3.2, U1.7 (AINA-)
unnamed: C16.2, C17.1, R12.2, U1.6 (AINB+)
unnamed: C15.2, C16.1, R9.2, U1.5 (AINB-)
unnamed: C13.1, U1.9 (REFCAP)
unnamed: C12.1, R13.2, U1.11 (REFIO)
unnamed: C14.1, U1.3 (REGCAP)
unnamed: C18.2, R11.2, U2.2 (+FB)
unnamed: C11.1, R7.2, R8.1, U2.24 (+IN)
unnamed: R12.1, U2.18 (+OUT)
unnamed: C11.2, R8.2, U2.23 (-FB)
unnamed: C18.1, R10.2, R11.1, U2.1 (-IN)
unnamed: R9.1, U2.19 (-OUT)
unnamed: C5.2, R5.2, U2.8 (+FB)
unnamed: C1.1, R1.2, R2.1, U2.6 (+IN)
unnamed: R6.1, U2.12 (+OUT)
unnamed: C1.2, R2.2, U2.5 (-FB)
unnamed: C5.1, R4.2, R5.1, U2.7 (-IN)
unnamed: R3.1, U2.13 (-OUT)
unnamed: C24.2, C25.1, R20.2, U3.8 (AINA+)
unnamed: C23.2, C24.1, R17.2, U3.7 (AINA-)
unnamed: C37.2, C38.1, R26.2, U3.6 (AINB+)
unnamed: C36.2, C37.1, R23.2, U3.5 (AINB-)
unnamed: C34.1, U3.9 (REFCAP)
unnamed: C33.1, R27.2, U3.11 (REFIO)
unnamed: C35.1, U3.3 (REGCAP)
unnamed: C39.2, R25.2, U4.2 (+FB)
unnamed: C32.1, R21.2, R22.1, U4.24 (+IN)
unnamed: R26.1, U4.18 (+OUT)
unnamed: C32.2, R22.2, U4.23 (-FB)
unnamed: C39.1, R24.2, R25.1, U4.1 (-IN)
unnamed: R23.1, U4.19 (-OUT)
unnamed: C26.2, R19.2, U4.8 (+FB)
unnamed: C22.1, R15.2, R16.1, U4.6 (+IN)
unnamed: R20.1, U4.12 (+OUT)
unnamed: C22.2, R16.2, U4.5 (-FB)
unnamed: C26.1, R18.2, R19.1, U4.7 (-IN)
unnamed: R17.1, U4.13 (-OUT)
unnamed: C45.2, C46.1, R34.2, U5.8 (AINA+)
unnamed: C44.2, C45.1, R31.2, U5.7 (AINA-)
unnamed: C58.2, C59.1, R40.2, U5.6 (AINB+)
unnamed: C57.2, C58.1, R37.2, U5.5 (AINB-)
unnamed: C55.1, U5.9 (REFCAP)
unnamed: C54.1, R41.2, U5.11 (REFIO)
unnamed: C56.1, U5.3 (REGCAP)
unnamed: C60.2, R39.2, U6.2 (+FB)
unnamed: C53.1, R35.2, R36.1, U6.24 (+IN)
unnamed: R40.1, U6.18 (+OUT)
unnamed: C53.2, R36.2, U6.23 (-FB)
unnamed: C60.1, R38.2, R39.1, U6.1 (-IN)
unnamed: R37.1, U6.19 (-OUT)
unnamed: C47.2, R33.2, U6.8 (+FB)
unnamed: C43.1, R29.2, R30.1, U6.6 (+IN)
unnamed: R34.1, U6.12 (+OUT)
unnamed: C43.2, R30.2, U6.5 (-FB)
unnamed: C47.1, R32.2, R33.1, U6.7 (-IN)
unnamed: R31.1, U6.13 (-OUT)
unnamed: C66.2, C67.1, R48.2, U7.8 (AINA+)
unnamed: C65.2, C66.1, R45.2, U7.7 (AINA-)
unnamed: C79.2, C80.1, R54.2, U7.6 (AINB+)
unnamed: C78.2, C79.1, R51.2, U7.5 (AINB-)
unnamed: C76.1, U7.9 (REFCAP)
unnamed: C75.1, R55.2, U7.11 (REFIO)
unnamed: C77.1, U7.3 (REGCAP)
unnamed: C81.2, R53.2, U8.2 (+FB)
unnamed: C74.1, R49.2, R50.1, U8.24 (+IN)
unnamed: R54.1, U8.18 (+OUT)
unnamed: C74.2, R50.2, U8.23 (-FB)
unnamed: C81.1, R52.2, R53.1, U8.1 (-IN)
unnamed: R51.1, U8.19 (-OUT)
unnamed: C68.2, R47.2, U8.8 (+FB)
unnamed: C64.1, R43.2, R44.1, U8.6 (+IN)
unnamed: R48.1, U8.12 (+OUT)
unnamed: C64.2, R44.2, U8.5 (-FB)
unnamed: C68.1, R46.2, R47.1, U8.7 (-IN)
unnamed: R45.1, U8.13 (-OUT)
unnamed: R61.1, U10.46 (USB_DN)
unnamed: R60.1, U10.47 (USB_DP)
unnamed: C87.1, U10.20 (XIN), X1.3 (C2)
unnamed: R64.1, U10.21 (XOUT)
unnamed: C93.1, R65.2, U10.43 (ADC_VDD)
unnamed: R66.1, R67.2, U13.2 (SENSE/ADJ)
unnamed: R68.1, R69.2, R70.2, U15.2 (NC/ADJ)
unnamed: C86.1, R64.2, X1.1 (C1)
OPT_EN_VN: U10.12 (GPIO09), U15.3 (EN)
OPT_EN_VP: U10.11 (GPIO08), U13.4 (EN)
QSPI_SCLK: U9.6 (CLK), U10.52 (QSPI_SCLK)
QSPI_SD0: U9.5 (DI/IO[0]), U10.53 (QSPI_SD0)
QSPI_SD1: U9.2 (DO/IO[1]), U10.55 (QSPI_SD1)
QSPI_SD2: U9.3 (#WP/IO[2]), U10.54 (QSPI_SD2)
QSPI_SD3: U9.7 (#HOLD/IO[3]), U10.51 (QSPI_SD3)
QSPI_SS_N: R57.2, R58.1, U9.1 (/CS), U10.56 (QSPI_SS_N)
RUN: J5.B7 (13), R59.1, U10.26 (RUN)
SCLK_A1: U1.16 (SCLK), U10.28 (GPIO17)
SCLK_A2: U3.16 (SCLK), U10.38 (GPIO26/ADC0)
SCLK_A3: J2.10, U5.16 (SCLK), U10.16 (GPIO13)
SCLK_A4: U7.16 (SCLK), U10.34 (GPIO22)
SDI_A1: U1.15 (SDI), U10.29 (GPIO18)
SDI_A2: U3.15 (SDI), U10.39 (GPIO27/ADC1)
SDI_A3: J2.8, U5.15 (SDI), U10.17 (GPIO14)
SDI_A4: U7.15 (SDI), U10.35 (GPIO23)
SDOA_A1: U1.13 (SDOA), U10.31 (GPIO20)
SDOA_A2: U3.13 (SDOA), U10.41 (GPIO29/ADC3)
SDOA_A3: J2.4, U5.13 (SDOA), U10.18 (GPIO15)
SDOA_A4: U7.13 (SDOA), U10.36 (GPIO24)
SDOB_A1: U1.14 (SDOB), U10.30 (GPIO19)
SDOB_A2: U3.14 (SDOB), U10.40 (GPIO28/ADC2)
SDOB_A3: J2.6, U5.14 (SDOB), U10.14 (GPIO11)
SDOB_A4: U7.14 (SDOB), U10.13 (GPIO10)
SWCLK: J3.1, J5.B6 (11), U10.24 (SWCLK)
SWDIO: J3.3, J5.B5 (9), U10.25 (SWDIO)
V1P1: C91.1, C96.1, C97.1, TP21.P$1 (P$1_P$1), U10.23 (DVDD), U10.45 (VREG_VOUT), U10.50 (DVDD)
V3P3: C7.1, C28.1, C49.1, C70.1, C85.1, C90.1, C92.1, C98.1, C99.1, C100.1, C101.1, C102.1, C103.1, C113.1, J5.B16 (31), R58.2, R59.2, R65.1, TP17.P$1 (P$1_P$1), U1.2 (VLOGIC), U3.2 (VLOGIC), U5.2 (VLOGIC), U7.2 (VLOGIC), U9.8 (VCC), U10.1 (IOVDD), U10.10 (IOVDD), U10.22 (IOVDD), U10.33 (IOVDD), U10.42 (IOVDD), U10.44 (VREG_VIN), U10.48 (USB_VDD), U10.49 (IOVDD), U11.1 (OUT)
V3P3A: C6.1, C8.1, C19.1, C27.1, C29.1, C40.1, C48.1, C50.1, C61.1, C69.1, C71.1, C82.1, C95.1, C111.1, TP18.P$1 (P$1_P$1), U1.4 (VCC), U2.3 (+VS), U2.4 (+VS), U2.9 (+VS), U2.10 (+VS), U3.4 (VCC), U4.3 (+VS), U4.4 (+VS), U4.9 (+VS), U4.10 (+VS), U5.4 (VCC), U6.3 (+VS), U6.4 (+VS), U6.9 (+VS), U6.10 (+VS), U7.4 (VCC), U8.3 (+VS), U8.4 (+VS), U8.9 (+VS), U8.10 (+VS), U12.1 (OUT)
V5P0: C88.1, C89.1, C94.1, D1.1 (K), D2.1 (K), TP22.P$1 (P$1_P$1), U11.5 (/SHDN), U11.8 (IN), U12.5 (/SHDN), U12.8 (IN)
V5P0_IN: D1.2 (A), D1.3 (A), J5.A1 (2), J5.A3 (6), J5.B1 (1), J5.B3 (5)
V6P5: C105.1, LF1.2, R66.2, U13.1 (VOUT)
V9P0: C104.1, J5.A18 (36), R71.2, U13.6 (VIN)
VBUS: D2.2 (A), D2.3 (A), J4.1
VN1P2: C10.1, C21.1, C31.1, C42.1, C52.1, C63.1, C73.1, C84.1, C107.2, C112.2, TP19.P$1 (P$1_P$1), U2.15 (-VS), U2.16 (-VS), U2.21 (-VS), U2.22 (-VS), U4.15 (-VS), U4.16 (-VS), U4.21 (-VS), U4.22 (-VS), U6.15 (-VS), U6.16 (-VS), U6.21 (-VS), U6.22 (-VS), U8.15 (-VS), U8.16 (-VS), U8.21 (-VS), U8.22 (-VS), U14.1 (OUT), U14.2 (NC/ADJ)
VN3P0: C106.2, J5.A19 (38), U14.3 (EN), U14.6 (IN), U14.PAD (IN)
VN20P0: C109.2, C110.2, LF2.2, R69.1, U15.1 (OUT)
VN22: C108.2, J5.B20 (39), U15.6 (IN), U15.PAD (IN)
VOCM_A1: C9.1, C20.1, R13.1, R14.2, TP5.P$1 (P$1_P$1), U2.11 (VOCM), U2.17 (VOCM)
VOCM_A2: C30.1, C41.1, R27.1, R28.2, TP8.P$1 (P$1_P$1), U4.11 (VOCM), U4.17 (VOCM)
VOCM_A3: C51.1, C62.1, R41.1, R42.2, TP12.P$1 (P$1_P$1), U6.11 (VOCM), U6.17 (VOCM)
VOCM_A4: C72.1, C83.1, R55.1, R56.2, TP16.P$1 (P$1_P$1), U8.11 (VOCM), U8.17 (VOCM)
/CS_A1: U1.12 (/CS), U10.27 (GPIO16)
/CS_A2: U3.12 (/CS), U10.37 (GPIO25)
/CS_A3: J2.2, U5.12 (/CS), U10.15 (GPIO12)
/CS_A4: U7.12 (/CS), U10.32 (GPIO21)

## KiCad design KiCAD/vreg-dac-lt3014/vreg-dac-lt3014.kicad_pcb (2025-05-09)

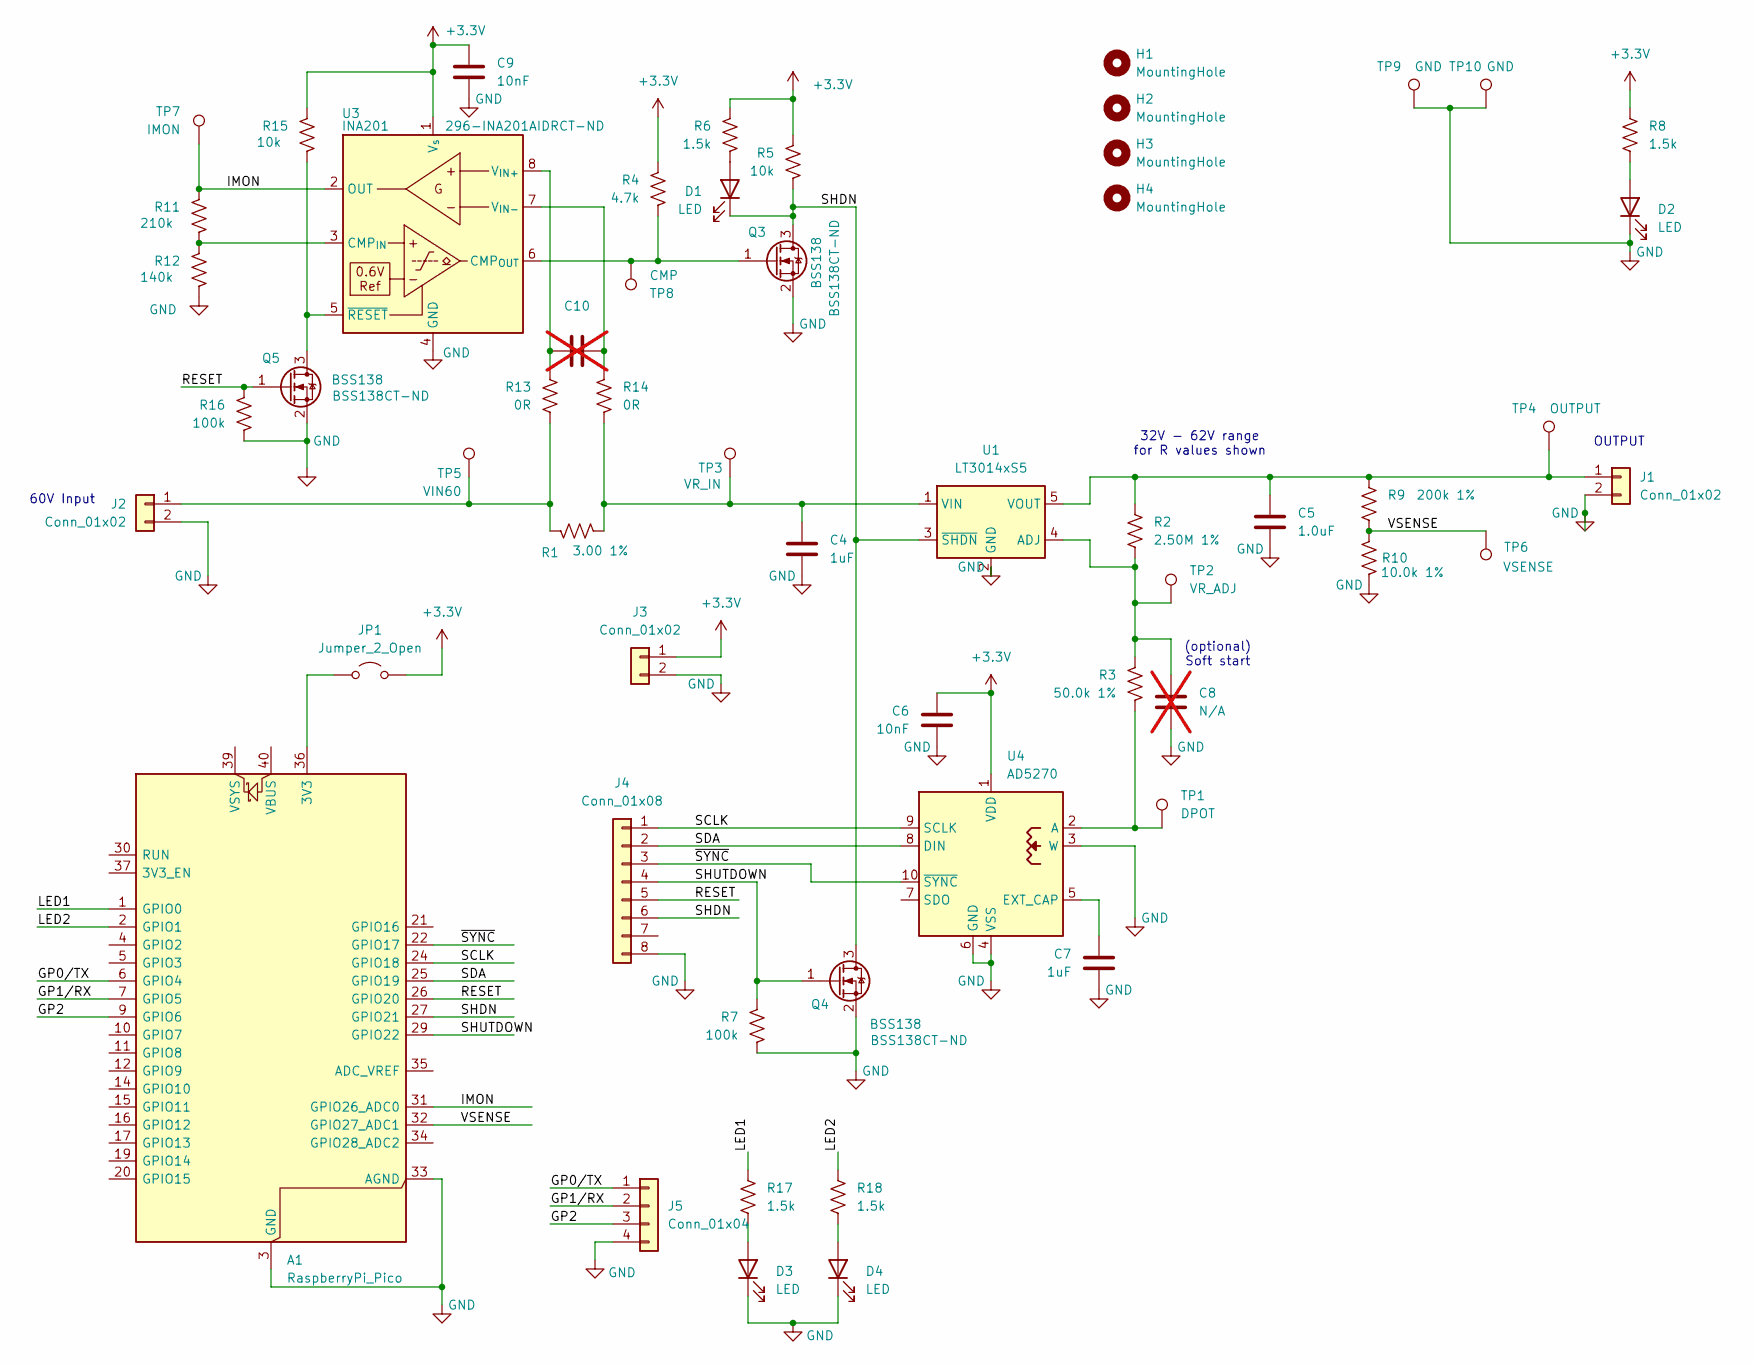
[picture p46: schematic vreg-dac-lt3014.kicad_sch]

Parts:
A1: RaspberryPi_Pico; RaspberryPi_Pico_Common_Unspecified
C4, C7: 1uF; C_0603_1608Metric_Pad1.08x0.95mm_HandSolder
C5: 1.0uF; C_0603_1608Metric_Pad1.08x0.95mm_HandSolder
C6, C9: 10nF; C_0603_1608Metric_Pad1.08x0.95mm_HandSolder
C8: N/A; C_0603_1608Metric_Pad1.08x0.95mm_HandSolder; not fitted
C10: C_0603_1608Metric_Pad1.08x0.95mm_HandSolder; not fitted
D1, D2, D3, D4: LED; my_SMT_0603
H1, H2, H3, H4: MountingHole; MountingHole_4.3mm_M4
J1, J2, J3: Conn_01x02; PinHeader_1x02_P2.54mm_Vertical
J4: Conn_01x08; PinHeader_1x08_P2.54mm_Vertical
J5: Conn_01x04; PinHeader_1x04_P2.54mm_Vertical
JP1: Jumper_2_Open; PinHeader_1x02_P2.54mm_Vertical
Q3, Q4, Q5: BSS138; SOT-23
R1: 3.00 1%; R_0603_1608Metric_Pad0.98x0.95mm_HandSolder
R2: 2.50M 1%; R_0603_1608Metric_Pad0.98x0.95mm_HandSolder
R3: 50.0k 1%; R_0603_1608Metric_Pad0.98x0.95mm_HandSolder
R4: 4.7k; R_0603_1608Metric_Pad0.98x0.95mm_HandSolder
R5, R15: 10k; R_0603_1608Metric_Pad0.98x0.95mm_HandSolder
R6, R8, R17, R18: 1.5k; R_0603_1608Metric_Pad0.98x0.95mm_HandSolder
R7, R16: 100k; R_0603_1608Metric_Pad0.98x0.95mm_HandSolder
R9: 200k 1%; R_0603_1608Metric_Pad0.98x0.95mm_HandSolder
R10: 10.0k 1%; R_0603_1608Metric_Pad0.98x0.95mm_HandSolder
R11: 210k; R_0603_1608Metric_Pad0.98x0.95mm_HandSolder
R12: 140k; R_0603_1608Metric_Pad0.98x0.95mm_HandSolder
R13, R14: 0R; R_0603_1608Metric_Pad0.98x0.95mm_HandSolder
TP1: DPOT; tp_SMT_label2
TP2: VR_ADJ; tp_SMT_label2
TP3: VR_IN; tp_SMT_label2
TP4: OUTPUT; tp_SMT_label2
TP5: VIN60; tp_SMT_label2
TP6: VSENSE; tp_SMT_label2
TP7: IMON; tp_SMT_label2
TP8: CMP; tp_SMT_label2
TP9, TP10: GND; tp_SMT_label2
U1: LT3014xS5; SOT-23-5
U3: INA201; SOIC-8_3.9x4.9mm_P1.27mm
U4: AD5270; MSOP-10_3x3mm_P0.5mm

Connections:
+3.3V: C6.1, C9.1, J3.1, JP1.2 (B), R4.1, R5.1, R6.1, R8.1, R15.1, U3.1 (V_{s}), U4.1 (VDD)
/GP0/TX: A1.6 (GPIO4), J5.1
/GP1/RX: A1.7 (GPIO5), J5.2
/GP2: A1.9 (GPIO6), J5.3
/IMON: A1.31 (GPIO26_ADC0), R11.1, TP7.1, U3.2 (OUT)
/LED1: A1.1 (GPIO0), R17.1
/LED2: A1.2 (GPIO1), R18.1
/RESET: A1.26 (GPIO20), J4.5, Q5.1 (G), R16.1
/SCLK: A1.24 (GPIO18), J4.1, U4.9 (SCLK)
/SDA: A1.25 (GPIO19), J4.2, U4.8 (DIN)
/SHDN: A1.27 (GPIO21), D1.1 (K), J4.6, Q3.3 (D), Q4.3 (D), R5.2, U1.3 (~SHDN)
/SHUTDOWN: A1.29 (GPIO22), J4.4, Q4.1 (G), R7.1
/VSENSE: A1.32 (GPIO27_ADC1), R9.2, R10.1, TP6.1
/~SYNC: A1.22 (GPIO17), J4.3, U4.10 (~SYNC)
GND: A1.3 (GND), A1.8 (GND), A1.13 (GND), A1.18 (GND), A1.23 (GND), A1.28 (GND), A1.33 (AGND), A1.38 (GND), C4.2, C5.2, C6.2, C7.2, C8.2, C9.2, D2.1 (K), D3.1 (K), D4.1 (K), J1.2, J2.2, J3.2, J4.8, J5.4, Q3.2 (S), Q4.2 (S), Q5.2 (S), R7.2, R10.2, R12.2, R16.2, TP9.1, TP10.1, U1.2 (GND), U3.4 (GND), U4.3 (W), U4.4 (VSS), U4.6 (GND)
unnamed: A1.36 (3V3), JP1.1 (A)
unnamed: D1.2 (A), R6.2
unnamed: D2.2 (A), R8.2
unnamed: D3.2 (A), R17.2
unnamed: D4.2 (A), R18.2
unnamed: C5.1, J1.1, R2.1, R9.1, TP4.1, U1.5 (VOUT)
unnamed: J2.1, R1.1, R13.2, TP5.1
unnamed: Q3.1 (G), R4.2, TP8.1, U3.6 (CMP_{OUT})
unnamed: Q5.3 (D), R15.2, U3.5 (~RESET)
unnamed: C8.1, R2.2, R3.1, TP2.1, U1.4 (ADJ)
unnamed: C4.1, R1.2, R14.2, TP3.1, U1.1 (VIN)
unnamed: R11.2, R12.1, U3.3 (CMP_{IN})
unnamed: C10.1, R13.1, U3.8 (V_{IN+})
unnamed: C10.2, R14.1, U3.7 (V_{IN-})
unnamed: R3.2, TP1.1, U4.2 (A)
unnamed: C7.1, U4.5 (EXT_CAP)

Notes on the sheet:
OUTPUT
(optional) Soft start
60V Input
32V - 62V range for R values shown

Board: 4 copper layers, 56 parts (0 on the bottom side), 31 nets, no tracks yet.

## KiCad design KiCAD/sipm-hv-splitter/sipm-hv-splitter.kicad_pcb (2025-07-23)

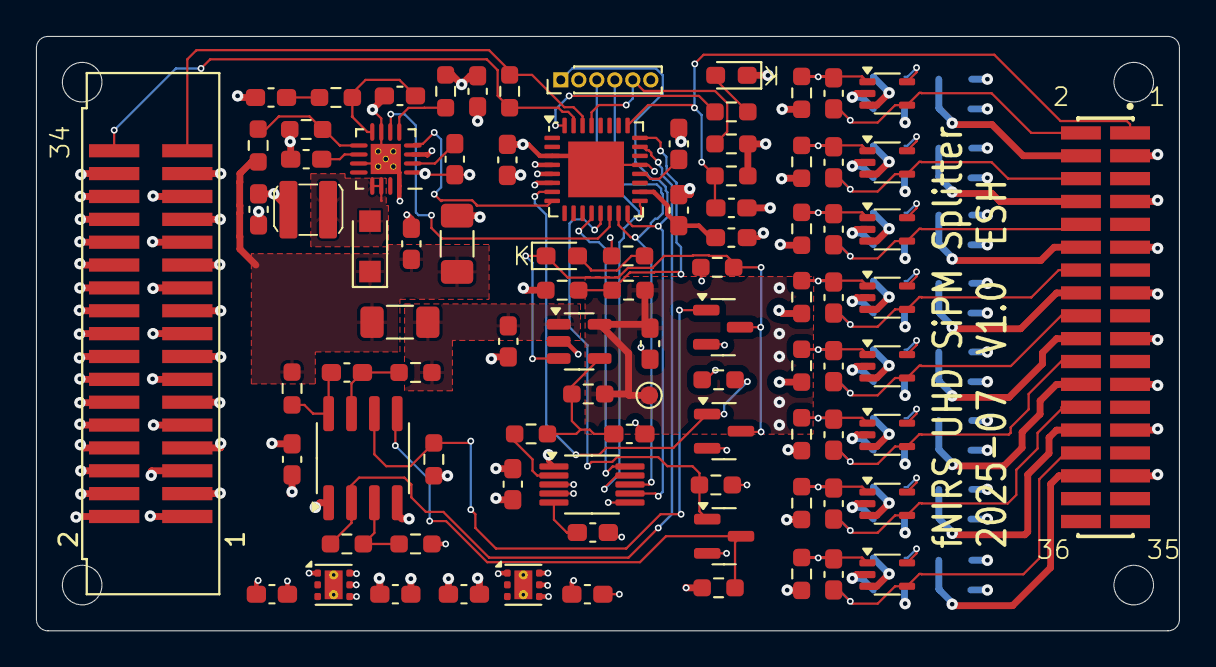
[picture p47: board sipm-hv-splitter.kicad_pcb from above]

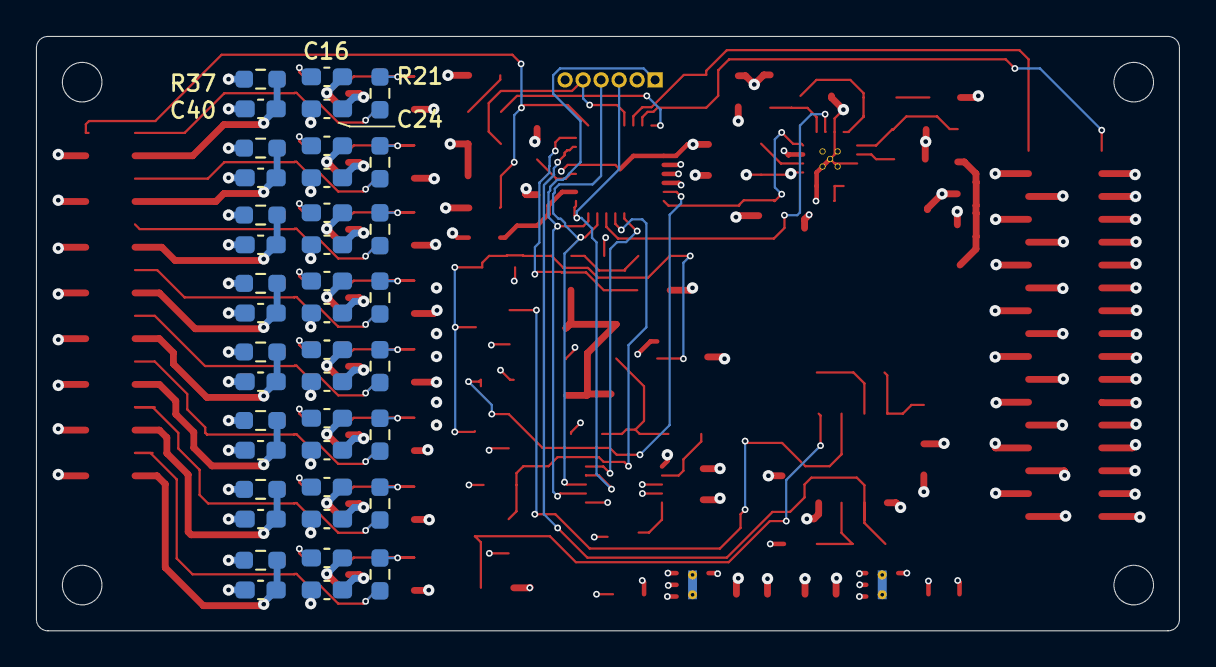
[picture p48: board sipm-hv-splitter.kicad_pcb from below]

Board: 6 copper layers, 63.5 x 33.0 mm, 133 parts (40 on the bottom side), 75 nets.

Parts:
C1: 4.7uF; C_0603_1608Metric_Pad1.08x0.95mm_HandSolder
C2, C3, C6, C48, C50, C52, C53: 1.0uF; C_0603_1608Metric_Pad1.08x0.95mm_HandSolder
C4, C16, C17, C18, C19, C20, C21, C22, C23, C24, C25, C26, C27, C28, C29, C30, C31, C40, C41, C42, C43, C44, C45, C46, C47, C54, C55: 0.1uF; C_0603_1608Metric_Pad1.08x0.95mm_HandSolder
C5, C13: 10nF; C_0603_1608Metric_Pad1.08x0.95mm_HandSolder
C7: 22nF; C_0603_1608Metric_Pad1.08x0.95mm_HandSolder
C8: 56pF; C_0603_1608Metric_Pad1.08x0.95mm_HandSolder
C9: 4.7uF 100V; C_1206_3216Metric_Pad1.33x1.80mm_HandSolder
C10: 0.1uF 100V; C_0603_1608Metric_Pad1.08x0.95mm_HandSolder
C11, C12, C14: 1.0uF 100V; C_0603_1608Metric_Pad1.08x0.95mm_HandSolder
C15: N/A; C_0603_1608Metric_Pad1.08x0.95mm_HandSolder
C32, C33, C34, C35, C36, C37, C38, C39: 1nF; C_0603_1608Metric_Pad1.08x0.95mm_HandSolder
C49, C51: 2.2uF; C_0603_1608Metric_Pad1.08x0.95mm_HandSolder
D1: MBR1H100SFT3G; Nexperia_CFP3_SOD-123W
D2, D3: LED; my_SMT_0603
H1, H2, H3, H4: MountingHole; MountingHole_2.2mm_M2
J1: Conn_02x18_Odd_Even; SAMTEC_SFMC-118-02-L-D
J2: Conn_02x17_Odd_Even; SHF-117-01-X-D-SM
J3: ISP; PinHeader_1x06_P1.00mm_Vertical
L1: 10uH; WE-TPC-ind
L2: 10uH; L_0603_1608Metric_Pad1.05x0.95mm_HandSolder
Q1, Q2, Q3: BSS138; SOT-23
R1, R37, R38, R39, R40, R41, R42, R43, R44: 1k; R_0603_1608Metric_Pad0.98x0.95mm_HandSolder
R2: 210k; R_0603_1608Metric_Pad0.98x0.95mm_HandSolder
R3: 140k; R_0603_1608Metric_Pad0.98x0.95mm_HandSolder
R4, R7: 100k; R_0603_1608Metric_Pad0.98x0.95mm_HandSolder
R5, R6, R16, R46: 10.0k; R_0603_1608Metric_Pad0.98x0.95mm_HandSolder
R8, R10: 100; R_0603_1608Metric_Pad0.98x0.95mm_HandSolder
R9: 3.00 1%; R_1206_3216Metric_Pad1.30x1.75mm_HandSolder
R11, R45: 4.7k; R_0603_1608Metric_Pad0.98x0.95mm_HandSolder
R12: 3.16k; R_0603_1608Metric_Pad0.98x0.95mm_HandSolder
R13: 150k; R_0603_1608Metric_Pad0.98x0.95mm_HandSolder
R14: 2.49k; R_0603_1608Metric_Pad0.98x0.95mm_HandSolder
R15, R47: 1.5k; R_0603_1608Metric_Pad0.98x0.95mm_HandSolder
R17: 2.50M 1%; R_0603_1608Metric_Pad0.98x0.95mm_HandSolder
R18: 510k 1%; R_0603_1608Metric_Pad0.98x0.95mm_HandSolder
R19: 24.0k 1%; R_0603_1608Metric_Pad0.98x0.95mm_HandSolder
R20: 50.0k 1%; R_0603_1608Metric_Pad0.98x0.95mm_HandSolder
R21, R22, R23, R24, R25, R26, R27, R28: 15k; R_0603_1608Metric_Pad0.98x0.95mm_HandSolder
R29, R30, R31, R32, R33, R34, R35, R36: 15; R_0603_1608Metric_Pad0.98x0.95mm_HandSolder
TP8: OUTPUT; TestPoint_Pad_D1.0mm
U1: ATmega328-M; QFN-32-1EP_5x5mm_P0.5mm_EP3.1x3.1mm
U2: INA201; SOIC-8_3.9x4.9mm_P1.27mm
U3: LM51581; QFN-16_EP_3x3_Pitch0.5mm
U4: LT3014xS5; SOT-23-5
U5: AD5270; MSOP-10_3x3mm_P0.5mm
U6, U7, U8, U9, U10, U11, U12, U13: OPA810xDCK; Texas_R-PDSO-G5_DCK-5
U14, U16: TPS7A25; WSON-6-1EP_2x2mm_P0.65mm_EP1x1.6mm_ThermalVias

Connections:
+3.3V: C5.1, C13.1, C49.1, C52.1, J3.2 (VCC), L2.1, R5.1, R7.1, R11.1, R15.1, R16.1, R45.2, R46.2, U1.4 (VCC), U1.6 (VCC), U2.1 (V_{s}), U5.1 (VDD), U16.1 (OUT)
+3.3VA: C16.1, C17.1, C18.1, C19.1, C20.1, C21.1, C22.1, C23.1, C51.1, U6.5 (V+), U7.5 (V+), U8.5 (V+), U9.5 (V+), U10.5 (V+), U11.5 (V+), U12.5 (V+), U13.5 (V+), U14.1 (OUT)
+12V: C1.1, C3.1, C48.1, C50.1, J2.1, J2.5, J2.9, J2.13, J2.17, J2.21, J2.25, J2.29, L1.1, U3.3 (BIAS), U14.4 (EN), U14.6 (IN), U16.4 (EN), U16.6 (IN)
-24V: C24.1, C25.1, C26.1, C27.1, C28.1, C29.1, C30.1, C31.1, J2.2, J2.6, J2.10, J2.14, J2.18, J2.22, J2.26, J2.30, U6.2 (V-), U7.2 (V-), U8.2 (V-), U9.2 (V-), U10.2 (V-), U11.2 (V-), U12.2 (V-), U13.2 (V-)
/ADC_IMON: R2.1, U1.23 (PC0), U2.2 (OUT)
/ADC_VMON: R18.2, R19.1, U1.24 (PC1)
/BOOST/62V: C9.1, C10.1, D1.1 (K), R8.2, R9.1, R13.1
/BOOST/SHDN: D2.1 (K), Q2.3 (D), Q3.3 (D), R16.2, U4.3 (~SHDN)
/BOOST/V62_IN: C11.1, R9.2, R10.2, U4.1 (VIN)
/BOOST_ENA: U1.14 (PB2), U3.6 (UVLO)
/COMM/RX: J2.33, R1.1, U1.30 (PD0)
/COMM/TX: J2.34, R1.2, U1.31 (PD1)
/DET_0: C39.1, J1.30, R28.1, U13.4 (-)
/DET_1: C38.1, J1.26, R27.1, U12.4 (-)
/DET_2: C37.1, J1.22, R26.1, U11.4 (-)
/DET_3: C36.1, J1.18, R25.1, U10.4 (-)
/DET_4: C35.1, J1.14, R24.1, U9.4 (-)
/DET_5: C34.1, J1.10, R23.1, U8.4 (-)
/DET_6: C33.1, J1.6, R22.1, U7.4 (-)
/DET_7: C32.1, J1.2, R21.1, U6.4 (-)
/MISO: J3.1 (MISO), U1.16 (PB4), U5.7 (SDO)
/MOSI: J3.4 (MOSI), U1.15 (PB3), U5.8 (DIN)
/PGOOD: U1.8 (XTAL2/PB7), U3.4 (PGOOD)
/SCK: J3.3 (SCK), U1.17 (PB5), U5.9 (SCLK)
/SIG_0: J2.4, R36.2
/SIG_1: J2.8, R35.2
/SIG_2: J2.12, R34.2
/SIG_3: J2.16, R33.2
/SIG_4: J2.20, R32.2
/SIG_5: J2.24, R31.2
/SIG_6: J2.28, R30.2
/SIG_7: J2.32, R29.2
/THERM: C53.1, J1.1, R46.1, U1.25 (PC2)
/TIA_0/SIPM_K: C40.1, J1.4, R37.2
/TIA_1/SIPM_K: C41.1, J1.8, R38.2
/TIA_2/SIPM_K: C42.1, J1.12, R39.2
/TIA_3/SIPM_K: C43.1, J1.16, R40.2
/TIA_4/SIPM_K: C44.1, J1.20, R41.2
/TIA_5/SIPM_K: C45.1, J1.24, R42.2
/TIA_6/SIPM_K: C46.1, J1.28, R43.2
/TIA_7/SIPM_K: C47.1, J1.32, R44.2
/VBIAS: C12.1, R17.1, R18.1, R37.1, R38.1, R39.1, R40.1, R41.1, R42.1, R43.1, R44.1, TP8.1, U4.5 (VOUT)
/VR_RESET: Q1.1 (G), R4.1, U1.13 (PB1)
/VR_SHDN: Q3.1 (G), R7.2, U1.7 (XTAL1/PB6)
/~RESET: J3.5 (~RST), R45.1, U1.29 (~RESET/PC6)
/~SYNC: U1.12 (PB0), U5.10 (~SYNC)
GND: C1.2, C2.2, C3.2, C4.2, C5.2, C7.2, C8.2, C9.2, C10.2, C11.2, C12.2, C13.2, C14.2, C15.2, C16.2, C17.2, C18.2, C19.2, C20.2, C21.2, C22.2, C23.2, C24.2, C25.2, C26.2, C27.2, C28.2, C29.2, C30.2, C31.2, C40.2, C41.2, C42.2, C43.2, C44.2, C45.2, C46.2, C47.2, C48.2, C49.2, C50.2, C51.2, C52.2, C53.2, C54.2, C55.2, D3.1 (K), J1.3, J1.7, J1.11, J1.15, J1.19, J1.23, J1.27, J1.31, J2.3, J2.7, J2.11, J2.15, J2.19, J2.23, J2.27, J2.31, J3.6 (GND), Q1.2 (S), Q2.2 (S), Q3.2 (S), R3.2, R4.2, R6.2, R14.2, R19.2, U1.3 (GND), U1.5 (GND), U1.21 (GND), U1.33 (GND), U2.4 (GND), U3.1 (PGND), U3.7 (AGND), U3.11 (MODE), U3.16 (PGND), U3.17 (EP/GND), U4.2 (GND), U5.3 (W), U5.4 (VSS), U5.6 (GND), U6.3 (+), U7.3 (+), U8.3 (+), U9.3 (+), U10.3 (+), U11.3 (+), U12.3 (+), U13.3 (+), U14.5 (GND), U14.7 (Pad), U16.5 (GND), U16.7 (Pad)
unnamed: C7.1, R12.2
unnamed: C32.2, R21.2, R29.1, U6.1
unnamed: C33.2, R22.2, R30.1, U7.1
unnamed: C34.2, R23.2, R31.1, U8.1
unnamed: C35.2, R24.2, R32.1, U9.1
unnamed: C36.2, R25.2, R33.1, U10.1
unnamed: C37.2, R26.2, R34.1, U11.1
unnamed: C38.2, R27.2, R35.1, U12.1
unnamed: C39.2, R28.2, R36.1, U13.1
unnamed: D1.2 (A), L1.2, U3.13 (SW), U3.14 (SW)
unnamed: D2.2 (A), R15.2
unnamed: D3.2 (A), R47.2
unnamed: Q1.3 (D), R5.2, U2.5 (~RESET)
unnamed: Q2.1 (G), R11.2, U2.6 (CMP_{OUT})
unnamed: C55.1, U1.20 (AREF)
unnamed: C54.1, L2.2, U1.18 (AVCC)
unnamed: R47.1, U1.32 (PD2)
unnamed: R2.2, R3.1, U2.3 (CMP_{IN})
unnamed: C6.1, R8.1, U2.8 (V_{IN+})
unnamed: C6.2, R10.1, U2.7 (V_{IN-})
unnamed: C8.1, R12.1, U3.8 (COMP)
unnamed: R13.2, R14.1, U3.9 (FB)
unnamed: R6.1, U3.5 (RT)
unnamed: C4.1, U3.10 (SS)
unnamed: C2.1, U3.2 (VCC)
unnamed: C15.1, R17.2, R20.1, U4.4 (ADJ)
unnamed: R20.2, U5.2 (A)
unnamed: C14.1, U5.5 (EXT_CAP)

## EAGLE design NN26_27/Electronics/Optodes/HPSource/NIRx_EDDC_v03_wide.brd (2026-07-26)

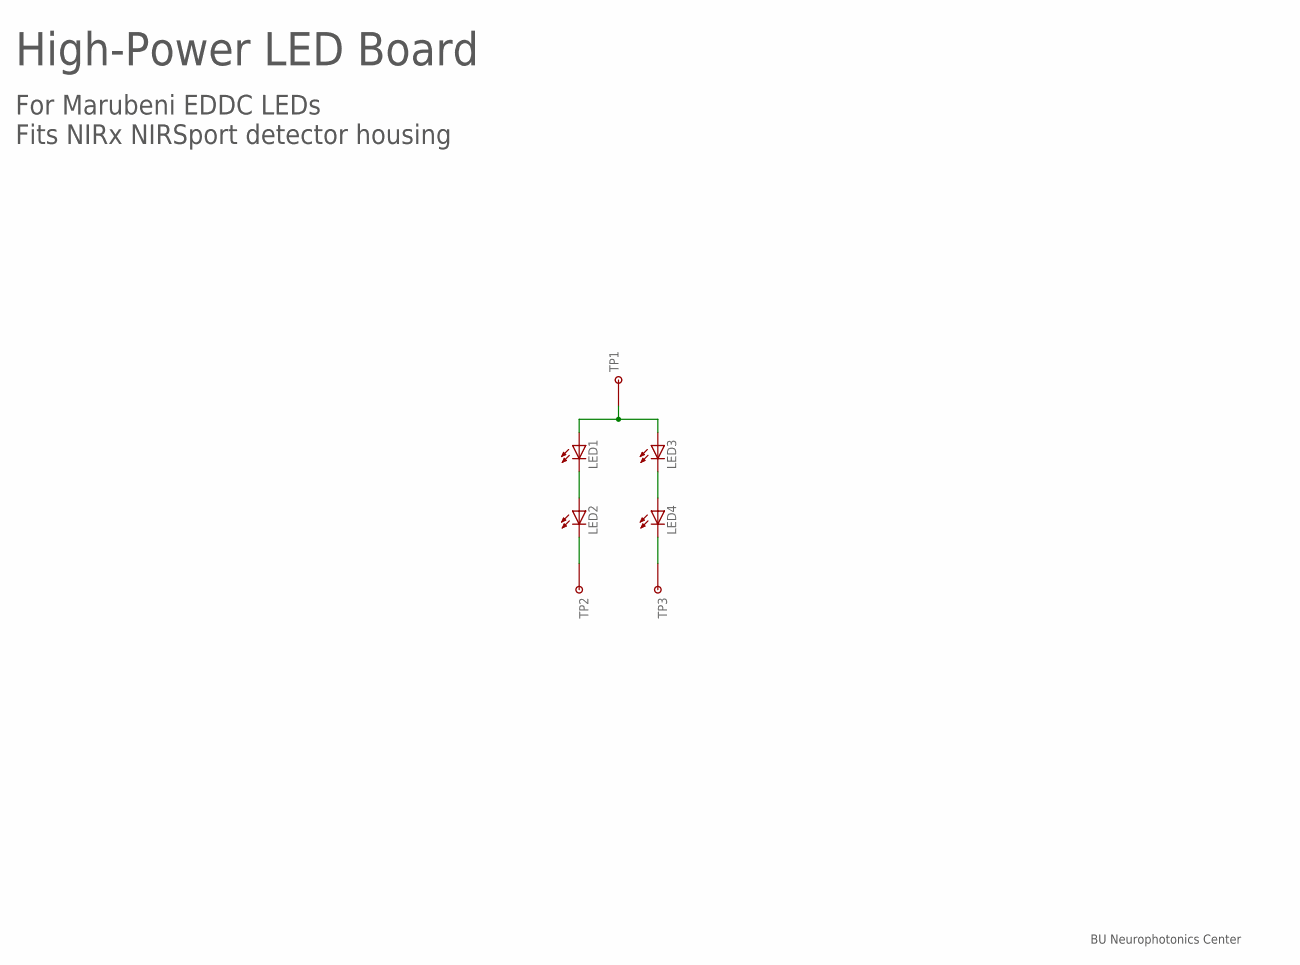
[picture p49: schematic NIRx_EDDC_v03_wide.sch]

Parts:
LED1, LED2, LED3, LED4: LED_EDCC; MARUBENI_EDCC
TP1, TP2, TP3: TESTPOINT_PADMEDIUM; TESTPAD_MEDIUM

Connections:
76: LED2.C, TP2.P$1
85: LED4.C, TP3.P$1
AN: LED1.A, LED3.A, TP1.P$1
I76: LED1.C, LED2.A
I85: LED3.C, LED4.A

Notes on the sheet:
High-Power LED Board
For Marubeni EDDC LEDs Fits NIRx NIRSport detector housing
BU Neurophotonics Center

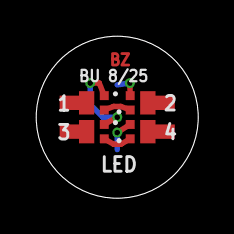
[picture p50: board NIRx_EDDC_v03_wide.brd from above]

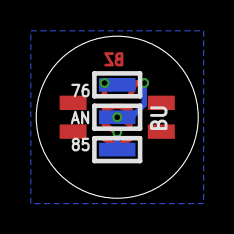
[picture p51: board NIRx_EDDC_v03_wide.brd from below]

Board: 2 copper layers, 9.0 x 9.0 mm, 7 parts (3 on the bottom side), 5 nets.

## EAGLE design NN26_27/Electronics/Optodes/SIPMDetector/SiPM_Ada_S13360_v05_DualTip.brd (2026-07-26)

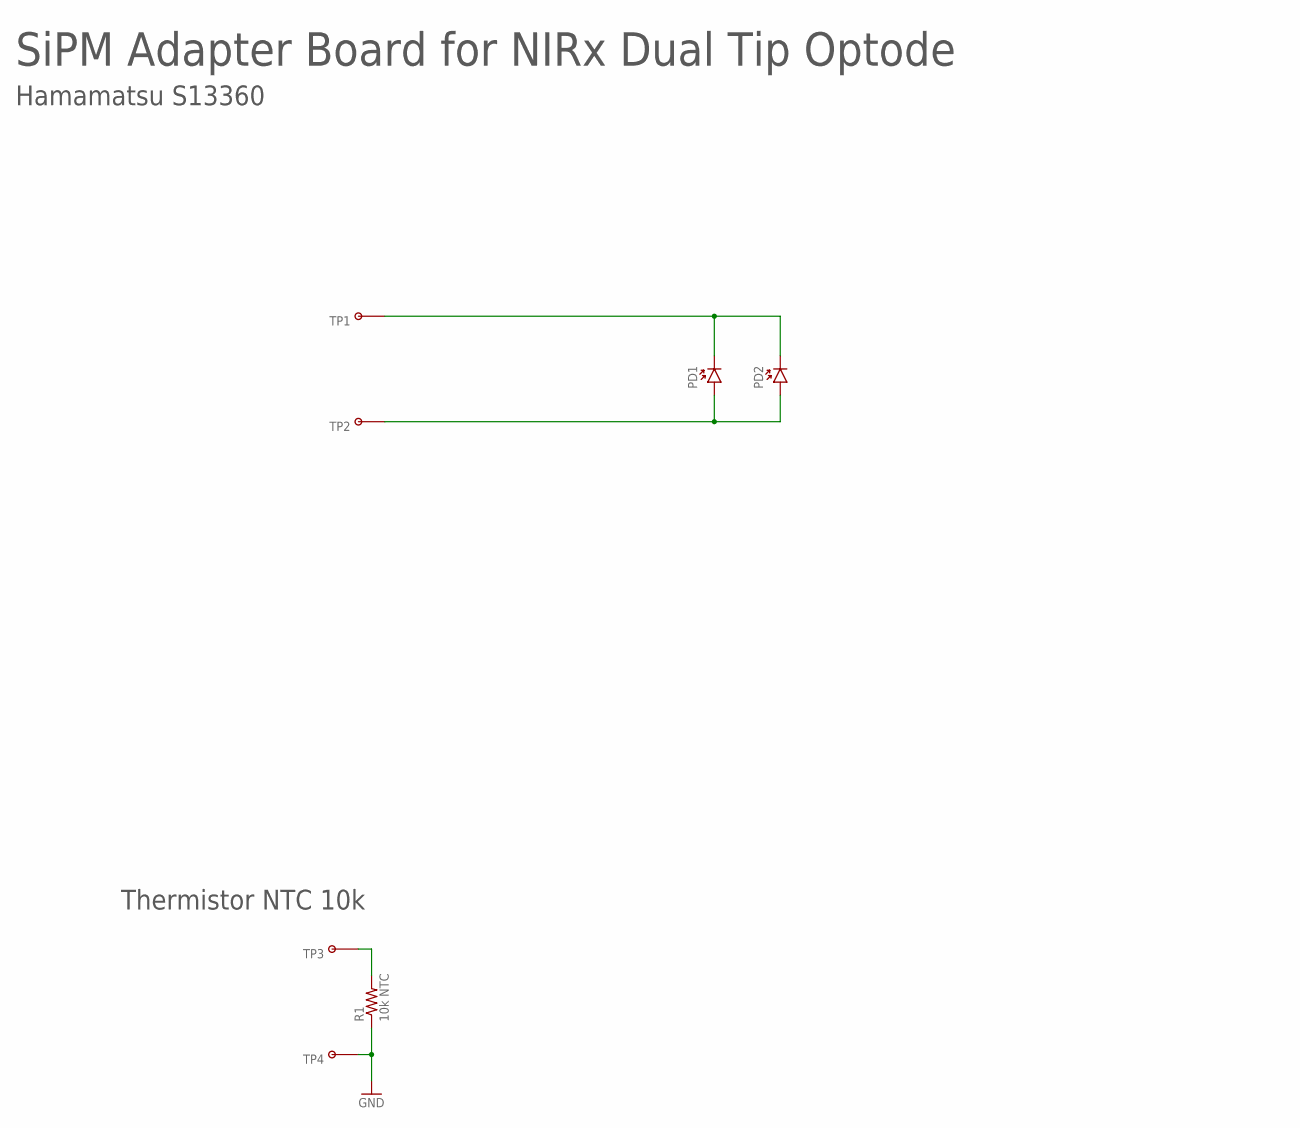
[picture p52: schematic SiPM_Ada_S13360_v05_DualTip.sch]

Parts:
PD1, PD2: PHOTODIODE_S13360-30XXPE; S13360-30XXPE
R1: 10k NTC; 0603-RES
TP1, TP2, TP3, TP4: TESTPOINT_PADMEDIUM; TESTPAD_MEDIUM

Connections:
A: PD1.A, PD2.A, TP2.P$1
C: PD1.C, PD2.C, TP1.P$1
GND: R1.1, TP4.P$1
T: R1.2, TP3.P$1

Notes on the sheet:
SiPM Adapter Board for NIRx Dual Tip Optode
Hamamatsu S13360
Thermistor NTC 10k

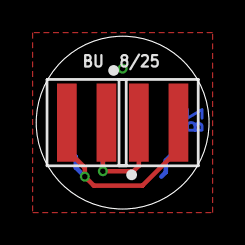
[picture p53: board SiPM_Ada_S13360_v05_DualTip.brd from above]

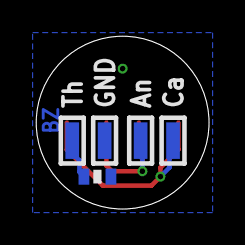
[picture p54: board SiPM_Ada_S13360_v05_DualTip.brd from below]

Board: 2 copper layers, 9.6 x 9.6 mm, 7 parts (5 on the bottom side), 4 nets.

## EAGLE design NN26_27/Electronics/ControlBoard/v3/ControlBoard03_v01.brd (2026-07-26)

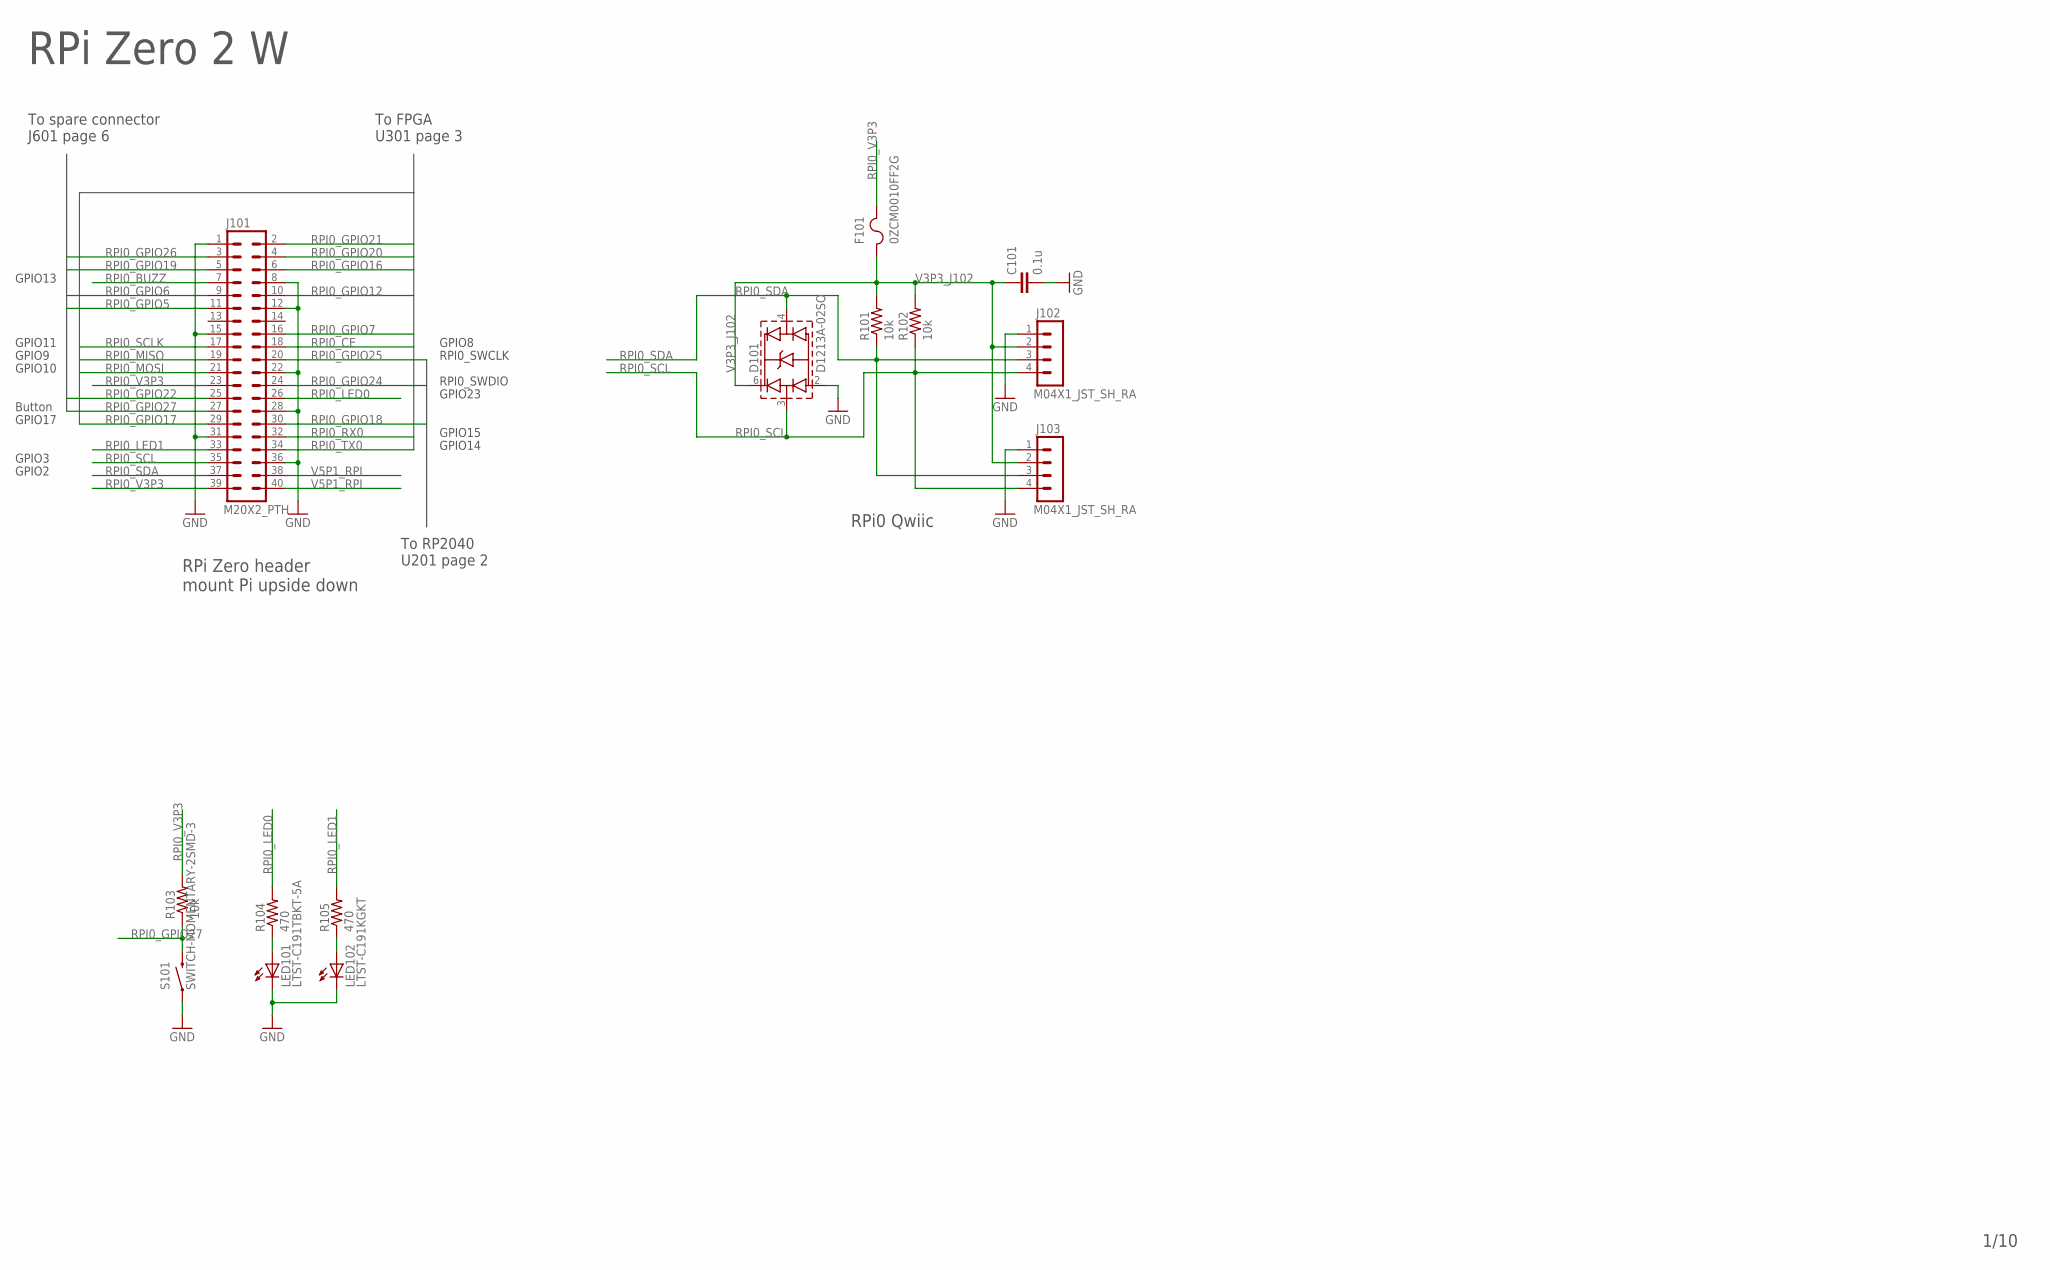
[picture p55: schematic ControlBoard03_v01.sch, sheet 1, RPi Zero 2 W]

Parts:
C101: 0.1u; 0402-CAP
D101: D1213A-02SO; SOT23-6
F101: 0ZCM0010FF2G; 0603-RES
J101: M20X2_PTH
J102, J103: M04X1_JST_SH_RA; M04X1_JST_SH_SM_RA
LED101: LTST-C191TBKT-5A; LED-0603
LED102: LTST-C191KGKT; LED-0603
R101, R102, R103: 10k; 0402-RES
R104, R105: 470; 0402-RES
S101: SWITCH-MOMENTARY-2SMD-3; TACTILE_SWITCH_SMD-3

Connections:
GND: C101.2, D101.2 (VN), J101.1, J101.8, J101.12, J101.15, J101.22, J101.28, J101.31, J101.36, J102.1, J103.1, LED101.C, LED102.C, S101.1; also elsewhere on the board
unnamed: LED101.A, R104.1
unnamed: LED102.A, R105.1
RPI0_BUZZ: J101.7; also elsewhere on the board
RPI0_CE: J101.18; also elsewhere on the board
RPI0_GPIO5: J101.11; also elsewhere on the board
RPI0_GPIO6: J101.9; also elsewhere on the board
RPI0_GPIO7: J101.16; also elsewhere on the board
RPI0_GPIO12: J101.10; also elsewhere on the board
RPI0_GPIO16: J101.6; also elsewhere on the board
RPI0_GPIO17: J101.29; also elsewhere on the board
RPI0_GPIO18: J101.30; also elsewhere on the board
RPI0_GPIO19: J101.5; also elsewhere on the board
RPI0_GPIO20: J101.4; also elsewhere on the board
RPI0_GPIO21: J101.2; also elsewhere on the board
RPI0_GPIO22: J101.25; also elsewhere on the board
RPI0_GPIO24: J101.24; also elsewhere on the board
RPI0_GPIO25: J101.20; also elsewhere on the board
RPI0_GPIO26: J101.3; also elsewhere on the board
RPI0_GPIO27: J101.27, R103.1, S101.4 (2); also elsewhere on the board
RPI0_LED0: J101.26, R104.2
RPI0_LED1: J101.33, R105.2
RPI0_MISO: J101.19; also elsewhere on the board
RPI0_MOSI: J101.21; also elsewhere on the board
RPI0_RX0: J101.32; also elsewhere on the board
RPI0_SCL: D101.3 (CH1), J101.35, J102.4, J103.4, R102.1; also elsewhere on the board
RPI0_SCLK: J101.17; also elsewhere on the board
RPI0_SDA: D101.4 (CH2), J101.37, J102.3, J103.3, R101.1; also elsewhere on the board
RPI0_TX0: J101.34; also elsewhere on the board
RPI0_V3P3: F101.2, J101.23, J101.39, R103.2
V3P3_J102: C101.1, D101.6 (VP), F101.1, J102.2, J103.2, R101.2, R102.2
V5P1_RPI: J101.38, J101.40; also elsewhere on the board

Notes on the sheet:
GPIO15
GPIO14
RPI0_SWDIO
RPI0_SWCLK
GPIO8
GPIO11
GPIO9
GPIO10
GPIO2
GPIO3
GPIO13
RPi Zero 2 W
RPi Zero header mount Pi upside down
RPi0 Qwiic
GPIO23
Button
To spare connector J601 page 6
To FPGA U301 page 3
To RP2040 U201 page 2
GPIO17


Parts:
C201, C202, C203, C204, C207, C208: 0.1u; 0402-CAP
C205, C206: 27p; 0402-CAP
D201, D202, D204: D1213A-02SO; SOT23-6
D203, D205: DIODE_SOD523; SOD523
F201, F202, F203, F204: 0ZCM0010FF2G; 0603-RES
J201, J202: M04X1_JST_SH_RA; M04X1_JST_SH_SM_RA
J203: USB-MICRO
J204, J205: M04X2_0.050_SMD_NO_CREAM
J206, J208: M03POLAR; MOLEX-1X3
J207: M03X1_JST_SH; M03X1_JST_SH_SM
LED201: LTST-C191KRKT; LED-0603
LED202: LTST-C191KGKT; LED-0603
LED203: LTST-C191KSKT; LED-0603
Q201, Q202: MOSFET-NCHANNELSMD; SOT23-3
R201: 1k; 0402-RES
R202, R212, R214: DNP; 0402-RES
R203, R204, R207, R208, R210, R218: 10k; 0402-RES
R205, R217, R221, R225, R227: 100k; 0402-RES
R206: 47k; 0402-RES
R209, R211: 27; 0402-RES
R213: 1.2k; 0402-RES
R215, R216, R219, R220, R222, R226, R228: 470; 0402-RES
R223, R224: 100; 0402-RES
S201, S202: SWITCH-MOMENTARY-2SMD-3; TACTILE_SWITCH_SMD-3
TP201, TP202: TESTPOINT_ROUND; TESTPAD_ROUND
U201: RP2040; QFN-56_EP
U202: W25Q_USON_PAD; USON8L-2X3MM_APM
X201: 403I35D12M00000; CRYSTAL-3.2-2.5

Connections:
BOOTSEL: R201.1, S201.4 (2)
FAN1_EN: R222.1, U201.36 (GPIO24)
FAN1_SENSE: D204.4 (CH2), R220.1, U201.37 (GPIO25)
FAN2_EN: R228.1, U201.2 (GPIO00)
FAN2_SENSE: R226.1, U201.3 (GPIO01)
GND: C201.2, C202.2, C203.2, C204.2, C205.2, C206.2, C207.2, C208.2, D201.2 (VN), D202.2 (VN), D204.2 (VN), J201.1, J202.1, J203.5, J203.SH1, J203.SH2, J203.SH3, J203.SH4, J203.SH5, J203.SH6, J204.1, J204.3, J204.5, J204.7, J205.1, J205.3, J205.5, J205.7, J207.2, LED201.C, LED202.C, LED203.C, Q201.2 (S), Q202.2 (S), R210.1, R217.1, R218.1, R227.1, S201.1, U201.19 (TESTEN), U202.4 (GND), X201.2 (GND), X201.4 (GND); also elsewhere on the board
unnamed: C206.1, U201.20 (XIN), X201.3 (C2)
unnamed: C205.1, R213.2, X201.1 (C1)
unnamed: R213.1, U201.21 (XOUT)
unnamed: R209.1, U201.47 (USB_DP)
unnamed: R211.1, U201.46 (USB_DN)
unnamed: J203.2, R211.2
unnamed: J203.3, R209.2
unnamed: LED203.A, R219.1
unnamed: J206.3, R220.2, R221.1
unnamed: LED202.A, R216.1
unnamed: LED201.A, R215.1
unnamed: D203.A, J206.1, Q201.3 (D)
unnamed: Q201.1 (G), R217.2, R222.2
unnamed: D205.A, J208.1, Q202.3 (D)
unnamed: J208.3, R225.1, R226.2
unnamed: Q202.1 (G), R227.2, R228.2
QSPI_SCLK: U201.52 (QSPI_SCLK), U202.6 (CLK)
QSPI_SD0: U201.53 (QSPI_SD0), U202.5 (DI/IO[0])
QSPI_SD1: U201.55 (QSPI_SD1), U202.2 (DO/IO[1])
QSPI_SD2: U201.54 (QSPI_SD2), U202.3 (#WP/IO[2])
QSPI_SD3: U201.51 (QSPI_SD3), U202.7 (#HOLD/IO[3])
QSPI_SS_N: R201.2, R202.1, U201.56 (QSPI_SS_N), U202.1 (/CS)
RPFP_D0: J205.2, U201.15 (GPIO12); also elsewhere on the board
RPFP_D1: J205.4, U201.16 (GPIO13); also elsewhere on the board
RPFP_D2: J205.6, U201.17 (GPIO14); also elsewhere on the board
RPFP_D3: J205.8, U201.18 (GPIO15); also elsewhere on the board
RPFP_D4: U201.27 (GPIO16); also elsewhere on the board
RPFP_D5: U201.28 (GPIO17); also elsewhere on the board
RPFP_D6: U201.29 (GPIO18); also elsewhere on the board
RPFP_D7: U201.30 (GPIO19); also elsewhere on the board
RPFP_D8: J204.2, U201.31 (GPIO20); also elsewhere on the board
RPFP_D9: J204.4, U201.32 (GPIO21); also elsewhere on the board
RPFP_D10: J204.6, U201.34 (GPIO22); also elsewhere on the board
RPFP_D11: J204.8, U201.35 (GPIO23); also elsewhere on the board
RPFP_RUN: R205.1, TP201.P$1, U201.26 (RUN); also elsewhere on the board
RPI0_GPIO18: U201.4 (GPIO02); also elsewhere on the board
RPI0_GPIO24: R212.1; also elsewhere on the board
RPI0_GPIO25: R214.1; also elsewhere on the board
RPIP_AUXIO0: U201.41 (GPIO29/ADC3); also elsewhere on the board
RPIP_AUXIO1: U201.39 (GPIO27/ADC1); also elsewhere on the board
RPIP_BTN: R218.2, S202.1, U201.8 (GPIO06)
RPIP_BUZZ: U201.9 (GPIO07); also elsewhere on the board
RPIP_LED0: R215.2, U201.7 (GPIO05)
RPIP_LED1: R216.2, U201.6 (GPIO04)
RPIP_LED2: R219.2, U201.5 (GPIO03)
RPIP_SCL0: D201.3 (CH1), J201.4, R204.1, U201.12 (GPIO09)
RPIP_SCL1: D202.3 (CH1), J202.4, R208.1, U201.14 (GPIO11); also elsewhere on the board
RPIP_SDA0: D201.4 (CH2), J201.3, R203.1, U201.11 (GPIO08)
RPIP_SDA1: D202.4 (CH2), J202.3, R207.1, U201.13 (GPIO10); also elsewhere on the board
SWCLK: J207.1, R214.2, R223.2
SWCLK_PRE: R223.1, U201.24 (SWCLK)
SWDIO: J207.3, R212.2, R224.2
SWDIO_PRE: R224.1, U201.25 (SWDIO)
V3P3: C202.1, D201.6 (VP), D202.6 (VP), D204.6 (VP), F201.1, F202.1, R202.2, R203.2, R204.2, R205.2, R207.2, R208.2, R221.2, R225.2, S202.4 (2), U202.8 (VCC); also elsewhere on the board
V3P3_J201: C201.1, F201.2, J201.2
V3P3_J202: C203.1, F202.2, J202.2
V12: F203.1, F204.1, R206.2; also elsewhere on the board
V12_CURR_SENSE: U201.38 (GPIO26/ADC0); also elsewhere on the board
V12_FAN1: C207.1, D203.C, F203.2, J206.2
V12_FAN2: C208.1, D205.C, F204.2, J208.2
VBUS: J203.1, TP202.P$1
VIN_SENSE: C204.1, D204.3 (CH1), R206.1, R210.2, U201.40 (GPIO28/ADC2)

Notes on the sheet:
BOOTSEL (force USB boot)
CTS-Frequency Controls 403I35D12M00000
RP2040 MCU (RPi Pico)
RPiP Qwiic0
RPiP Qwiic1
Debug
To RPi 0 J101 page 1
To RPi 0 J101 page 1
To FPGA U301 page 3
To Aux Coax J505 page 5
MISO
SCLK
MOSI
UART_ACC_TO_FPGA
UART_FPGA_TO_ACC
ACC_BOARD_SELECT
ACC_END_CYC
ACC_STATUS_SELECT
ACC_RUN_IND
Fan
Fan 2

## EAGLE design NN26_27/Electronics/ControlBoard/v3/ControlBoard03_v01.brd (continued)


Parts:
C301: 0.1u; 0402-CAP
J301: M04X2_0.050_SMD_NO_CREAM
J302: M03X2PTH; 2X3-NS
J303, J304: M05X2_SMD_0.050_NOCREAM; M05X2_0.050_SMD_NO_CREAM
LED301, LED305: LTST-C191KRKT; LED-0603
LED302, LED306: LTST-C191KGKT; LED-0603
LED303: LTST-C191TBKT-5A; LED-0603
LED304: LTST-C191KSKT; LED-0603
R301, R302, R305, R306, R307, R312: 10k; 0402-RES
R303, R304: DNP; 0402-RES
R308, R309, R310, R311, R313, R314: 470; 0402-RES
TP301, TP303: TESTPOINT_ROUND; TESTPAD_ROUND
TP302: TESTPOINTPADSMALL; TESTPAD_SMALL
U301: MACHXO2_FTBGA256; LBGA-256
XO301: OSCILLATOR_TXO2520; TXO2520

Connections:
ADS_CSN0: U301.H5 (PL9C); also elsewhere on the board
ADS_CSN1: U301.C1 (PL2C); also elsewhere on the board
ADS_SCK0: U301.F5 (PL5C); also elsewhere on the board
ADS_SCK1: U301.B1 (PL1C); also elsewhere on the board
ADS_SDO0: U301.G5 (PL4C); also elsewhere on the board
ADS_SDO1: U301.C2 (PL1D); also elsewhere on the board
AUXIO0: U301.B3 (PT9C); also elsewhere on the board
AUXIO1: U301.A3 (PT11C); also elsewhere on the board
AUXIO2: U301.H13 (PR6C); also elsewhere on the board
DETB_END_CYC0: U301.R7 (PB9A); also elsewhere on the board
DETB_END_CYC1: U301.P1 (PL13D); also elsewhere on the board
DETB_END_CYC2: U301.J1 (PL7C/PCLKT4_0); also elsewhere on the board
DETB_END_CYC3: U301.D1 (PL1B/L_GPLLC_FB); also elsewhere on the board
DETB_RUN0: U301.T5 (PB6A); also elsewhere on the board
DETB_RUN1: U301.N3 (PL14B); also elsewhere on the board
DETB_RUN2: U301.K5 (PL12C); also elsewhere on the board
DETB_RUN3: U301.E3 (PL2B/L_GPLLC_IN); also elsewhere on the board
DETB_SELECT00: U301.R9 (PB18A); also elsewhere on the board
DETB_SELECT01: U301.R11 (PB22A); also elsewhere on the board
DETB_SELECT02: U301.T9 (PB16A/PCLKT2_1); also elsewhere on the board
DETB_SELECT03: U301.N9 (PB16D); also elsewhere on the board
DETB_SELECT04: U301.N11 (PB21D); also elsewhere on the board
DETB_SELECT05: U301.P9 (PB16B/PCLKC2_1); also elsewhere on the board
DETB_SELECT06: U301.T2 (PB3C); also elsewhere on the board
DETB_SELECT07: U301.T4 (PB3B); also elsewhere on the board
DETB_SELECT08: U301.R4 (PB6D); also elsewhere on the board
DETB_SELECT09: U301.P5 (PB5B); also elsewhere on the board
DETB_SELECT10: U301.N8 (PB12C); also elsewhere on the board
DETB_SELECT11: U301.N6 (PB8C); also elsewhere on the board
DETB_SELECT12: U301.K2 (PL10B); also elsewhere on the board
DETB_SELECT13: U301.M2 (PL14A); also elsewhere on the board
DETB_SELECT14: U301.M1 (PL12B/PCLKC3_0); also elsewhere on the board
DETB_SELECT15: U301.J4 (PL9D); also elsewhere on the board
DETB_SELECT16: U301.L4 (PL12D); also elsewhere on the board
DETB_SELECT17: U301.L3 (PL11B); also elsewhere on the board
DETB_SELECT18: U301.F2 (PL3B/PCLKC5_0); also elsewhere on the board
DETB_SELECT19: U301.H2 (PL6B); also elsewhere on the board
DETB_SELECT20: U301.G1 (PL6A); also elsewhere on the board
DETB_SELECT21: U301.F4 (PL3C); also elsewhere on the board
DETB_SELECT22: U301.H4 (PL6C); also elsewhere on the board
DETB_SELECT23: U301.G3 (PL5B); also elsewhere on the board
DETB_STATUS_SELECT0: U301.R6 (PB6B); also elsewhere on the board
DETB_STATUS_SELECT1: U301.N2 (PL13C); also elsewhere on the board
DETB_STATUS_SELECT2: U301.J2 (PL9A); also elsewhere on the board
DETB_STATUS_SELECT3: U301.D2 (PL2D); also elsewhere on the board
DETB_TRIGGER0: U301.T7 (PB11A/PCLKT2_0); also elsewhere on the board
DETB_TRIGGER1: U301.P2 (PL14D); also elsewhere on the board
DETB_TRIGGER2: U301.J3 (PL7D/PCLKC4_0); also elsewhere on the board
DETB_TRIGGER3: U301.E2 (PL2A/L_GPLLT_IN); also elsewhere on the board
EXP_J303_D0: J303.2, U301.C5 (PT10B/HS)
EXP_J303_D1: J303.4, U301.D6 (PT12A/HS)
EXP_J303_D2: J303.6, U301.D7 (PT13D)
EXP_J303_D3: J303.8, U301.C7 (PT13B/HS)
EXP_J304_D0: J304.2, U301.H16 (PR7B/PCLKC1_0)
EXP_J304_D1: J304.4, U301.H15 (PR6B)
EXP_J304_D2: J304.6, U301.G16 (PR6A)
EXP_J304_D3: J304.8, U301.G15 (PR5A)
EXP_J601_D0: U301.C10 (PT20C/JTAGENB); also elsewhere on the board
EXP_J601_D1: U301.B10 (PT20D/PROGRAMN); also elsewhere on the board
EXP_J601_D2: U301.A13 (PT24C/INITN); also elsewhere on the board
EXP_J601_D3: U301.E10 (PT20B/HS); also elsewhere on the board
EXP_J601_D4: U301.D11 (PT21D); also elsewhere on the board
EXP_J601_D5: U301.C12 (PT23A/HS); also elsewhere on the board
EXP_J601_D6: U301.C13 (PT24D/DONE); also elsewhere on the board
FP_LED0: R308.2, U301.A15 (PT24B/HS)
FP_LED1: R309.2, U301.B14 (PT24A/HS)
FP_LED2: R310.2, U301.A14 (PT22D)
FP_LED3: R311.2, U301.B13 (PT22C)
FP_LED4: R313.2, U301.K13 (PR11C)
FP_LED5: R314.2, U301.J13 (PR9D)
FP_SCL: R301.1, R303.1, U301.A9 (PT18C/SCL/PCLKT0_0)
FP_SDA: R302.1, R304.1, U301.C9 (PT18D/SDA/PCLKC0_0)
GND: C301.2, J301.1, J301.3, J301.5, J301.7, J302.6, J303.1, J303.3, J303.5, J303.7, J303.9, J304.1, J304.3, J304.5, J304.7, J304.9, LED301.C, LED302.C, LED303.C, LED304.C, LED305.C, LED306.C, R312.1, XO301.2 (GND); also elsewhere on the board
J901_SPARE0: U301.J12 (PR6D); also elsewhere on the board
J901_SPARE1: U301.K12 (PR11D); also elsewhere on the board
J901_SPARE2: U301.K14 (PR10A); also elsewhere on the board
unnamed: LED301.A, R308.1
unnamed: LED302.A, R309.1
unnamed: LED303.A, R310.1
unnamed: LED304.A, R311.1
unnamed: LED305.A, R313.1
unnamed: LED306.A, R314.1
OSC_CLK: U301.C8 (PT17A/HS/PCLKT0_1), XO301.3 (OUT)
RAM0_CEN: U301.K16 (PR9B); also elsewhere on the board
RAM0_SCLK: U301.K15 (PR10B); also elsewhere on the board
RAM0_SIO0: U301.L16 (PR11A); also elsewhere on the board
RAM0_SIO1: U301.J15 (PR9A); also elsewhere on the board
RAM0_SIO2: U301.J16 (PR7C); also elsewhere on the board
RAM0_SIO3: U301.L15 (PR12A); also elsewhere on the board
RPFP_D0: U301.B16 (PR1D); also elsewhere on the board
RPFP_D1: U301.C15 (PR1C); also elsewhere on the board
RPFP_D2: U301.C16 (PR2C); also elsewhere on the board
RPFP_D3: U301.D15 (PR2D); also elsewhere on the board
RPFP_D4: U301.D16 (PR2A); also elsewhere on the board
RPFP_D5: U301.E14 (PR2B); also elsewhere on the board
RPFP_D6: U301.E15 (PR1B); also elsewhere on the board
RPFP_D7: U301.E16 (PR3A); also elsewhere on the board
RPFP_D8: U301.T6 (PB8B/SO/SPISO); also elsewhere on the board
RPFP_D9: U301.R12 (PB25A/SN); also elsewhere on the board
RPFP_D10: U301.P6 (PB8A/MCLK/CCLK); also elsewhere on the board
RPFP_D11: U301.P13 (PB25B/SI/SISPI); also elsewhere on the board
RPFP_RUN: U301.H12 (PR5D); also elsewhere on the board
RPI0_CE: J301.6, U301.B11 (PT22A/HS); also elsewhere on the board
RPI0_GPIO7: U301.B12 (PT23B/HS); also elsewhere on the board
RPI0_GPIO12: U301.D9 (PT18B/HS); also elsewhere on the board
RPI0_GPIO16: U301.E9 (PT17D); also elsewhere on the board
RPI0_GPIO17: U301.F8 (PT18A/HS); also elsewhere on the board
RPI0_GPIO20: U301.D10 (PT20A/HS); also elsewhere on the board
RPI0_GPIO21: U301.C11 (PT21B/HS); also elsewhere on the board
RPI0_MISO: J301.4, U301.A11 (PT21A/HS); also elsewhere on the board
RPI0_MOSI: J301.2, U301.A10 (PT19B/HS); also elsewhere on the board
RPI0_RX0: U301.E8 (PT16B/HS); also elsewhere on the board
RPI0_SCL: R303.2; also elsewhere on the board
RPI0_SCLK: J301.8, U301.A12 (PT22B/HS); also elsewhere on the board
RPI0_SDA: R304.2; also elsewhere on the board
RPI0_TX0: U301.D8 (PT17C); also elsewhere on the board
SRCB_LED_EN: U301.M9 (PB18C); also elsewhere on the board
SRCB_NC0: U301.N15 (PR13C); also elsewhere on the board
SRCB_NC1: U301.M14 (PR13A); also elsewhere on the board
SRCB_RUN: U301.M11 (PB19D); also elsewhere on the board
SRCB_SELECT00: U301.L10 (PB18D); also elsewhere on the board
SRCB_SELECT01: U301.T13 (PB24B); also elsewhere on the board
SRCB_SELECT02: U301.T12 (PB22B); also elsewhere on the board
SRCB_SELECT03: U301.T14 (PB22D); also elsewhere on the board
SRCB_SELECT04: U301.P15 (PR14C); also elsewhere on the board
SRCB_SELECT05: U301.R16 (PR14D); also elsewhere on the board
SRCB_SELECT06: U301.N14 (PR14B); also elsewhere on the board
SRCB_SPARE: U301.L9 (PB12D); also elsewhere on the board
SRCB_STEP: U301.P11 (PB21B); also elsewhere on the board
TCK: J302.4, R312.2, U301.A7 (PT16C/TCK)
TDI: J302.3, R306.1, U301.A6 (PT12D/TDI)
TDO: J302.5, R305.1, U301.C6 (PT12C/TDO)
TMS: J302.2, R307.1, U301.B8 (PT16D/TMS)
TP301_NET: TP301.P$1, U301.H14 (PR7A/PCLKT1_0)
TP303_NET: TP303.P$1, U301.J11 (PR10C)
TRG0: U301.B4 (PT11D); also elsewhere on the board
TRG1: U301.A4 (PT10A/HS); also elsewhere on the board
TRG2: U301.B5 (PT9B/HS); also elsewhere on the board
TRG3: U301.A5 (PT11A/HS); also elsewhere on the board
UARTB_CTSN_TO_FTDI: U301.G13 (PR4D); also elsewhere on the board
UARTB_FPGA_TO_FTDI: U301.F16 (PR4B); also elsewhere on the board
UARTB_FTDI_TO_FPGA: U301.G12 (PR3D); also elsewhere on the board
UARTB_RTSN_TO_FPGA: U301.G14 (PR5B); also elsewhere on the board
UART_CTSN_TO_FTDI: U301.F15 (PR3B); also elsewhere on the board
UART_DETB_TO_FPGA00: U301.R10 (PB19B); also elsewhere on the board
UART_DETB_TO_FPGA01: U301.T8 (PB12B); also elsewhere on the board
UART_DETB_TO_FPGA02: U301.T10 (PB18B); also elsewhere on the board
UART_DETB_TO_FPGA03: U301.N10 (PB19C); also elsewhere on the board
UART_DETB_TO_FPGA04: U301.P8 (PB12A); also elsewhere on the board
UART_DETB_TO_FPGA05: U301.P10 (PB19A); also elsewhere on the board
UART_DETB_TO_FPGA06: U301.T3 (PB6C); also elsewhere on the board
UART_DETB_TO_FPGA07: U301.R3 (PB3D); also elsewhere on the board
UART_DETB_TO_FPGA08: TP302.P$1, U301.R5 (PB5A/CSSPIN); also elsewhere on the board
UART_DETB_TO_FPGA09: U301.N7 (PB9D); also elsewhere on the board
UART_DETB_TO_FPGA10: U301.P4 (PB3A); also elsewhere on the board
UART_DETB_TO_FPGA11: U301.P7 (PB9B); also elsewhere on the board
UART_DETB_TO_FPGA12: U301.L2 (PL12A/PCLKT3_0); also elsewhere on the board
UART_DETB_TO_FPGA13: U301.L1 (PL11A); also elsewhere on the board
UART_DETB_TO_FPGA14: U301.N1 (PL13B); also elsewhere on the board
UART_DETB_TO_FPGA15: U301.K4 (PL11C); also elsewhere on the board
UART_DETB_TO_FPGA16: U301.K3 (PL10A); also elsewhere on the board
UART_DETB_TO_FPGA17: U301.M3 (PL13A); also elsewhere on the board
UART_DETB_TO_FPGA18: U301.G2 (PL5A); also elsewhere on the board
UART_DETB_TO_FPGA19: U301.F1 (PL4B); also elsewhere on the board
UART_DETB_TO_FPGA20: U301.H1 (PL7B); also elsewhere on the board
UART_DETB_TO_FPGA21: U301.G4 (PL4D); also elsewhere on the board
UART_DETB_TO_FPGA22: U301.F3 (PL4A); also elsewhere on the board
UART_DETB_TO_FPGA23: U301.H3 (PL7A); also elsewhere on the board
UART_FPGA_TO_DETB0: U301.R8 (PB11B/PCLKC2_0); also elsewhere on the board
UART_FPGA_TO_DETB1: U301.R1 (PL14C); also elsewhere on the board
UART_FPGA_TO_DETB2: U301.K1 (PL9B); also elsewhere on the board
UART_FPGA_TO_DETB3: U301.E1 (PL3A/PCLKT5_0); also elsewhere on the board
UART_FPGA_TO_FTDI: U301.F14 (PR4A); also elsewhere on the board
UART_FPGA_TO_SRCB: U301.T11 (PB21A); also elsewhere on the board
UART_FTDI_TO_FPGA: U301.F12 (PR4C); also elsewhere on the board
UART_RTSN_TO_FPGA: U301.F13 (PR3C); also elsewhere on the board
UART_SRCB_TO_FPGA00: U301.P12 (PB24A); also elsewhere on the board
UART_SRCB_TO_FPGA01: U301.M10 (PB21C); also elsewhere on the board
UART_SRCB_TO_FPGA02: U301.R13 (PB22C); also elsewhere on the board
UART_SRCB_TO_FPGA03: U301.T15 (PB25C); also elsewhere on the board
UART_SRCB_TO_FPGA04: U301.R14 (PB25D); also elsewhere on the board
UART_SRCB_TO_FPGA05: U301.P16 (PR13D); also elsewhere on the board
UART_SRCB_TO_FPGA06: U301.N16 (PR14A); also elsewhere on the board
V3P3: C301.1, J302.1, J303.10, J304.10, R301.2, R302.2, R305.2, R306.2, R307.2, XO301.1 (EN), XO301.4 (VCC); also elsewhere on the board
V5P1_B01_EN: U301.M7 (PB9C); also elsewhere on the board
V5P1_B23_EN: U301.J5 (PL10C); also elsewhere on the board
V5P1_RPI_EN: U301.B7 (PT13A/HS); also elsewhere on the board
V5P1_SRC_EN: U301.L8 (PB11D); also elsewhere on the board
V9P0_EN: U301.M8 (PB16C); also elsewhere on the board
VN3P4_EN: U301.L14 (PR11B); also elsewhere on the board
VN22_CLKA: U301.M15 (PR13B); also elsewhere on the board
VN22_CLKB: U301.M16 (PR12B); also elsewhere on the board
VN22_EN: U301.L13 (PR12D); also elsewhere on the board
V_SRC_BOOST: U301.J14 (PR7D); also elsewhere on the board

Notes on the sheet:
XO 48 MHz ECS-2520MV-480-CN-TR
FPGA
FPGA JTAG
To RPi 0 J101 page 1
To RP2040 U201 page 2
To FTDI USB A601 page 6
To Spare Connector J601 page 6
To Remote Trigger Receiver JP601 page 6
To Aux ADCs U501 U503 page 5
To PSRAM U601, U602 page 6


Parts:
J401, J402, J403, J404, J405: M20X2_HARFLEX_M
R401, R403, R405, R407: 0; 0603-RES
R402, R404, R406, R408: DNP; 0603-RES

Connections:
DETB_END_CYC0: J402.B15 (29); also elsewhere on the board
DETB_END_CYC1: J403.B15 (29); also elsewhere on the board
DETB_END_CYC2: J404.B15 (29); also elsewhere on the board
DETB_END_CYC3: J405.B15 (29); also elsewhere on the board
DETB_RUN0: J402.A16 (32); also elsewhere on the board
DETB_RUN1: J403.A16 (32); also elsewhere on the board
DETB_RUN2: J404.A16 (32); also elsewhere on the board
DETB_RUN3: J405.A16 (32); also elsewhere on the board
DETB_SELECT00: J402.B11 (21); also elsewhere on the board
DETB_SELECT01: J402.B9 (17); also elsewhere on the board
DETB_SELECT02: J402.A10 (20); also elsewhere on the board
DETB_SELECT03: J402.B7 (13); also elsewhere on the board
DETB_SELECT04: J402.B5 (9); also elsewhere on the board
DETB_SELECT05: J402.A6 (12); also elsewhere on the board
DETB_SELECT06: J403.B11 (21); also elsewhere on the board
DETB_SELECT07: J403.B9 (17); also elsewhere on the board
DETB_SELECT08: J403.A10 (20); also elsewhere on the board
DETB_SELECT09: J403.B7 (13); also elsewhere on the board
DETB_SELECT10: J403.B5 (9); also elsewhere on the board
DETB_SELECT11: J403.A6 (12); also elsewhere on the board
DETB_SELECT12: J404.B11 (21); also elsewhere on the board
DETB_SELECT13: J404.B9 (17); also elsewhere on the board
DETB_SELECT14: J404.A10 (20); also elsewhere on the board
DETB_SELECT15: J404.B7 (13); also elsewhere on the board
DETB_SELECT16: J404.B5 (9); also elsewhere on the board
DETB_SELECT17: J404.A6 (12); also elsewhere on the board
DETB_SELECT18: J405.B11 (21); also elsewhere on the board
DETB_SELECT19: J405.B9 (17); also elsewhere on the board
DETB_SELECT20: J405.A10 (20); also elsewhere on the board
DETB_SELECT21: J405.B7 (13); also elsewhere on the board
DETB_SELECT22: J405.B5 (9); also elsewhere on the board
DETB_SELECT23: J405.A6 (12); also elsewhere on the board
DETB_STATUS_SELECT0: J402.B16 (31); also elsewhere on the board
DETB_STATUS_SELECT1: J403.B16 (31); also elsewhere on the board
DETB_STATUS_SELECT2: J404.B16 (31); also elsewhere on the board
DETB_STATUS_SELECT3: J405.B16 (31); also elsewhere on the board
DETB_TRIGGER0: J402.B14 (27); also elsewhere on the board
DETB_TRIGGER1: J403.B14 (27); also elsewhere on the board
DETB_TRIGGER2: J404.B14 (27); also elsewhere on the board
DETB_TRIGGER3: J405.B14 (27); also elsewhere on the board
GND: J401.A1 (2), J401.A9 (18), J401.A12 (24), J401.A13 (26), J401.A14 (28), J401.A15 (30), J401.A16 (32), J401.A17 (34), J401.A19 (38), J401.B1 (1), J401.B2 (3), J401.B3 (5), J401.B17 (33), J402.A1 (2), J402.A4 (8), J402.A8 (16), J402.A12 (24), J402.A13 (26), J402.A14 (28), J402.A15 (30), J402.A17 (34), J402.A19 (38), J402.B3 (5), J402.B4 (7), J402.B8 (15), J402.B12 (23), J402.B17 (33), J403.A1 (2), J403.A4 (8), J403.A8 (16), J403.A12 (24), J403.A13 (26), J403.A14 (28), J403.A15 (30), J403.A17 (34), J403.A19 (38), J403.B3 (5), J403.B4 (7), J403.B8 (15), J403.B12 (23), J403.B17 (33), J404.A1 (2), J404.A4 (8), J404.A8 (16), J404.A12 (24), J404.A13 (26), J404.A14 (28), J404.A15 (30), J404.A17 (34), J404.A19 (38), J404.B3 (5), J404.B4 (7), J404.B8 (15), J404.B12 (23), J404.B17 (33), J405.A1 (2), J405.A4 (8), J405.A8 (16), J405.A12 (24), J405.A13 (26), J405.A14 (28), J405.A15 (30), J405.A17 (34), J405.A19 (38), J405.B3 (5), J405.B4 (7), J405.B8 (15), J405.B12 (23), J405.B17 (33); also elsewhere on the board
SRCB_LED_EN: J401.B15 (29); also elsewhere on the board
SRCB_NC0: J401.A4 (8); also elsewhere on the board
SRCB_NC1: J401.A3 (6); also elsewhere on the board
SRCB_RUN: J401.B12 (23); also elsewhere on the board
SRCB_SELECT00: J401.B11 (21); also elsewhere on the board
SRCB_SELECT01: J401.B9 (17); also elsewhere on the board
SRCB_SELECT02: J401.A10 (20); also elsewhere on the board
SRCB_SELECT03: J401.B8 (15); also elsewhere on the board
SRCB_SELECT04: J401.B6 (11); also elsewhere on the board
SRCB_SELECT05: J401.A6 (12); also elsewhere on the board
SRCB_SELECT06: J401.B5 (9); also elsewhere on the board
SRCB_SPARE: J401.B16 (31); also elsewhere on the board
SRCB_STEP: J401.B14 (27); also elsewhere on the board
UART_DETB_TO_FPGA00: J402.B10 (19); also elsewhere on the board
UART_DETB_TO_FPGA01: J402.A11 (22); also elsewhere on the board
UART_DETB_TO_FPGA02: J402.A9 (18); also elsewhere on the board
UART_DETB_TO_FPGA03: J402.B6 (11); also elsewhere on the board
UART_DETB_TO_FPGA04: J402.A7 (14); also elsewhere on the board
UART_DETB_TO_FPGA05: J402.A5 (10); also elsewhere on the board
UART_DETB_TO_FPGA06: J403.B10 (19); also elsewhere on the board
UART_DETB_TO_FPGA07: J403.A11 (22); also elsewhere on the board
UART_DETB_TO_FPGA08: J403.A9 (18); also elsewhere on the board
UART_DETB_TO_FPGA09: J403.B6 (11); also elsewhere on the board
UART_DETB_TO_FPGA10: J403.A7 (14); also elsewhere on the board
UART_DETB_TO_FPGA11: J403.A5 (10); also elsewhere on the board
UART_DETB_TO_FPGA12: J404.B10 (19); also elsewhere on the board
UART_DETB_TO_FPGA13: J404.A11 (22); also elsewhere on the board
UART_DETB_TO_FPGA14: J404.A9 (18); also elsewhere on the board
UART_DETB_TO_FPGA15: J404.B6 (11); also elsewhere on the board
UART_DETB_TO_FPGA16: J404.A7 (14); also elsewhere on the board
UART_DETB_TO_FPGA17: J404.A5 (10); also elsewhere on the board
UART_DETB_TO_FPGA18: J405.B10 (19); also elsewhere on the board
UART_DETB_TO_FPGA19: J405.A11 (22); also elsewhere on the board
UART_DETB_TO_FPGA20: J405.A9 (18); also elsewhere on the board
UART_DETB_TO_FPGA21: J405.B6 (11); also elsewhere on the board
UART_DETB_TO_FPGA22: J405.A7 (14); also elsewhere on the board
UART_DETB_TO_FPGA23: J405.A5 (10); also elsewhere on the board
UART_FPGA_TO_DETB0: J402.B13 (25); also elsewhere on the board
UART_FPGA_TO_DETB1: J403.B13 (25); also elsewhere on the board
UART_FPGA_TO_DETB2: J404.B13 (25); also elsewhere on the board
UART_FPGA_TO_DETB3: J405.B13 (25); also elsewhere on the board
UART_FPGA_TO_SRCB: J401.B13 (25); also elsewhere on the board
UART_SRCB_TO_FPGA00: J401.B10 (19); also elsewhere on the board
UART_SRCB_TO_FPGA01: J401.A11 (22); also elsewhere on the board
UART_SRCB_TO_FPGA02: J401.A8 (16); also elsewhere on the board
UART_SRCB_TO_FPGA03: J401.B7 (13); also elsewhere on the board
UART_SRCB_TO_FPGA04: J401.A7 (14); also elsewhere on the board
UART_SRCB_TO_FPGA05: J401.A5 (10); also elsewhere on the board
UART_SRCB_TO_FPGA06: J401.B4 (7); also elsewhere on the board
V5P1_B01: J402.A18 (36), J402.A20 (40), J402.B18 (35), J402.B19 (37), J402.B20 (39), J403.A18 (36), J403.A20 (40), J403.B18 (35), J403.B19 (37), J403.B20 (39); also elsewhere on the board
V5P1_B23: J404.A18 (36), J404.A20 (40), J404.B18 (35), J404.B19 (37), J404.B20 (39), J405.A18 (36), J405.A20 (40), J405.B18 (35), J405.B19 (37), J405.B20 (39); also elsewhere on the board
V5P1_SRC: J401.A18 (36), J401.A20 (40), J401.B18 (35), J401.B19 (37), J401.B20 (39); also elsewhere on the board
V9P0: R401.1, R403.1, R405.1, R407.1; also elsewhere on the board
V9P0_B0: J402.A3 (6), R401.2, R402.2
V9P0_B1: J403.A3 (6), R403.2, R404.2
V9P0_B2: J404.A3 (6), R405.2, R406.2
V9P0_B3: J405.A3 (6), R407.2, R408.2
V60: R402.1, R404.1, R406.1, R408.1; also elsewhere on the board
VN3P4: J401.A2 (4), J402.A2 (4), J403.A2 (4), J404.A2 (4), J405.A2 (4); also elsewhere on the board
VN22: J402.B1 (1), J402.B2 (3), J403.B1 (1), J403.B2 (3), J404.B1 (1), J404.B2 (3), J405.B1 (1), J405.B2 (3); also elsewhere on the board

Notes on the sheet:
Backplane Connectors
Source Backplane
Detector Backplane B0
Detector Backplane B1
Detector Backplane B2
Detector Backplane B3


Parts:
C501, C504, C507, C508: 0.1u; 0402-CAP
C502, C509, C510: 4.7u; 0402-CAP
C503, C505: 10n; 0603-CAP
C506: 22u; 0805-CAP
D501, D502, D503: D1213A-02SO; SOT23-6
J501, J502, J503, J504, J505, J506: SMA_MMCX_PTH_RA; MMCX_PTH_RA
J507: U.FL
LF501: FERRITE1206; 1206
R501, R505: 1k; 0402-RES
R502, R506: 82; 0402-RES
R503, R507, R510, R513, R516, R518: DNP; 0805
R504, R508, R511, R514, R517, R519: 10k; 0402-RES
R509, R512, R515, R520, R521: 100; 0402-RES
TP501, TP502: TESTPOINT_ROUND; TESTPAD_ROUND
U501, U503: ADS7886; SOT363
U502: LT1801; SOP65P490X110-8N
U504: REF30XX; SOT23-3
U505: ADP7182_WSON; WSON6

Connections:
ADS_CSN0: U501.6 (CS#); also elsewhere on the board
ADS_CSN1: U503.6 (CS#); also elsewhere on the board
ADS_SCK0: U501.4 (SCLK); also elsewhere on the board
ADS_SCK1: U503.4 (SCLK); also elsewhere on the board
ADS_SDO0: U501.5 (SDO); also elsewhere on the board
ADS_SDO1: U503.5 (SDO); also elsewhere on the board
AUXIO0: D502.4 (CH2), R509.2; also elsewhere on the board
AUXIO1: D502.3 (CH1), R512.2; also elsewhere on the board
AUXIO2: R521.2; also elsewhere on the board
GND: C501.2, C502.2, C503.2, C504.2, C505.2, C506.2, C507.2, C508.1, C509.1, C510.1, D501.2 (VN), D502.2 (VN), D503.2 (VN), J501.G@1 (GND), J501.G@2 (GND), J501.G@3 (GND), J501.G@4 (GND), J502.G@1 (GND), J502.G@2 (GND), J502.G@3 (GND), J502.G@4 (GND), J503.G@1 (GND), J503.G@2 (GND), J503.G@3 (GND), J503.G@4 (GND), J504.G@1 (GND), J504.G@2 (GND), J504.G@3 (GND), J504.G@4 (GND), J505.G@1 (GND), J505.G@2 (GND), J505.G@3 (GND), J505.G@4 (GND), J506.G@1 (GND), J506.G@2 (GND), J506.G@3 (GND), J506.G@4 (GND), J507.P$1 (GND), J507.P$2 (GND), R503.1, R504.1, R507.1, R508.1, R510.1, R511.1, R513.1, R514.1, R516.1, R517.1, R518.1, R519.1, U501.2 (GND), U503.2 (GND), U504.3 (GND), U505.5 (GND); also elsewhere on the board
unnamed: J501.C (SIGNAL), R501.1, R503.2, R504.2
unnamed: D501.4 (CH2), R501.2, U502.5 (+IN)
unnamed: J502.C (SIGNAL), R505.1, R507.2, R508.2
unnamed: D501.3 (CH1), R505.2, U502.3 (+IN)
unnamed: J505.C (SIGNAL), R515.1, R516.2, R517.2
unnamed: J503.C (SIGNAL), R509.1, R510.2, R511.2
unnamed: J504.C (SIGNAL), R512.1, R513.2, R514.2
unnamed: C503.1, R502.2, U501.3 (VIN)
unnamed: R502.1, U502.6 (-IN), U502.7 (OUT)
unnamed: C505.1, R506.2, U503.3 (VIN)
unnamed: R506.1, U502.1 (OUT), U502.2 (-IN)
unnamed: J507.P$3 (SIGNAL), R521.1
unnamed: J506.C (SIGNAL), R518.2, R519.2, R520.1
unnamed: C506.1, LF501.2, U504.1 (IN)
RPIP_AUXIO0: D503.4 (CH2), R515.2; also elsewhere on the board
RPIP_AUXIO1: D503.3 (CH1), R520.2; also elsewhere on the board
V3P3: D502.6 (VP), D503.6 (VP); also elsewhere on the board
V5P1_B23: LF501.1; also elsewhere on the board
VA_3P3: C501.1, C502.1, C504.1, C507.1, D501.6 (VP), TP501.P$1, U501.1 (VDD), U502.8 (V+), U503.1 (VDD), U504.2 (OUT)
VN1P2: C508.2, C510.2, TP502.P$1, U502.4 (V-), U505.1 (OUT), U505.2 (NC/ADJ)
VN3P4: C509.2, U505.3 (EN), U505.6 (IN), U505.PAD (IN); also elsewhere on the board

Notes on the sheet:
many pin compatible alternatives e.g. TSV912
Aux I/O
REF3033 or NCP51460
To FPGA U301 page 3
To RP2040 U201 page 2

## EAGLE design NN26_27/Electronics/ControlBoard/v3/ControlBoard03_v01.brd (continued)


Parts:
C601, C602, C604, C605, C610: 4.7u; 0402-CAP
C603, C606, C607, C608, C613, C614, C615, C616, C617, C619, C620, C621, C622, C623, C624, C625, C626: 0.1u; 0402-CAP
C609: 22u; 0805-CAP
C611, C612: 27p; 0402-CAP
C618: DNP; 1210
D601: PACDN042; SOT23-3
D602: D1213A-02SO; SOT23-6
J601: USB-MICRO
J602: M04X2_0.050_SMD_NO_CREAM
J603: M13X2_0.050_SHF_NO_CREAM
J604: M07X1_PTH
LED601: LTST-C191KSKT; LED-0603
LED602, LED604: LTST-C191KGKT; LED-0603
LED603, LED605, LED606: LTST-C191KRKT; LED-0603
LF601, LF602: FERRITE0603; 0603-FER
LF603: FERRITE1206; 1206
LS601: PKMCS0909E4000-R1; XDCR_PKMCS0909E4000-R1
R601: 470; 0402-RES
R602, R606, R607, R608, R610, R612, R613, R614, R615, R616, R617, R619: 1k; 0402-RES
R603, R604, R605: 10k; 0402-RES
R609: 3.48k; 0402-RES
R611: 12k; 0402-RES
R618: 1M; R2010
TP601: TESTPOINT_ROUND; TESTPAD_ROUND
TP602: TESTPOINT1X01; 1X01
U601: MCP1755_DFN; DFN8_2X3MM
U602: 93LC56; SOT23-6
U603: APS6404L_PAD; USON8L-2X3MM_APM
U604: FT2232H_QFP; QFP50P1200X1200X160-64N
U605, U606: ISO7742_DBQ; SSOP16
X601: 403I35D12M00000; CRYSTAL-3.2-2.5

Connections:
EXP_J601_D0: J603.3; also elsewhere on the board
EXP_J601_D1: J603.5; also elsewhere on the board
EXP_J601_D2: J603.7; also elsewhere on the board
EXP_J601_D3: J603.9; also elsewhere on the board
EXP_J601_D4: J603.11; also elsewhere on the board
EXP_J601_D5: J603.13; also elsewhere on the board
EXP_J601_D6: J603.15; also elsewhere on the board
FTA_CTS#: U604.19 (ADBUS3), U605.13 (OUTB)
FTA_DSR#: U604.22 (ADBUS5)
FTA_DTR#: U604.21 (ADBUS4)
FTA_RTS#: U604.18 (ADBUS2), U605.11 (IND)
FTA_RXD: U604.17 (ADBUS1), U605.14 (OUTA)
FTA_RXLED#: R612.1, U604.29 (ACBUS3)
FTA_TXD: U604.16 (ADBUS0), U605.12 (INC)
FTA_TXLED#: R613.1, U604.30 (ACBUS4)
FTB_CTS#: U604.41 (BDBUS3), U606.13 (OUTB)
FTB_DSR#: U604.44 (BDBUS5)
FTB_DTR#: U604.43 (BDBUS4)
FTB_RTS#: U604.40 (BDBUS2), U606.11 (IND)
FTB_RXD: U604.39 (BDBUS1), U606.14 (OUTA)
FTB_RXLED#: R614.1, U604.54 (BCBUS3)
FTB_TXD: U604.38 (BDBUS0), U606.12 (INC)
FTB_TXLED#: R615.1, U604.55 (BCBUS4)
FT_PWREN#: U604.60 (!PWREN#)
FT_VREGOUT: C610.1, C624.1, C625.1, C626.1, U604.12 (VCORE), U604.37 (VCORE), U604.49 (VREGOUT), U604.64 (VCORE)
GND: C608.2, C609.2, C613.2, C614.2, C617.2, C618.1, J602.1, J602.3, J602.5, J602.7, J603.1, J603.2, J603.4, J603.6, J603.17, J603.21, J603.24, J603.25, J604.7, LED601.C, LS601.2, R618.1, U603.4 (GND), U605.2 (GND1), U605.8 (GND1), U606.2 (GND1), U606.8 (GND1); also elsewhere on the board
GNDI: C601.2, C602.2, C603.2, C604.2, C605.2, C606.2, C607.2, C610.2, C611.2, C612.2, C615.2, C616.2, C618.2, C619.2, C620.2, C621.2, C622.2, C623.2, C624.2, C625.2, C626.2, D601.3 (A), D602.2 (VN), J601.5, J601.SH1, J601.SH2, J601.SH3, J601.SH4, J601.SH5, J601.SH6, LED606.C, R611.1, R618.2, TP602.1, U601.4 (GND), U601.P (GND), U602.2 (GND), U604.1 (GND), U604.5 (GND), U604.10 (AGND), U604.11 (GND), U604.13 (TEST), U604.15 (GND), U604.25 (GND), U604.35 (GND), U604.47 (GND), U604.51 (GND), U605.9 (GND2), U605.15 (GND2), U606.9 (GND2), U606.15 (GND2), X601.2 (GND), X601.4 (GND)
LED: J604.1, R601.1
unnamed: LED606.A, R619.1
unnamed: R604.1, U602.5 (CS), U604.63 (EECS)
unnamed: R603.1, U602.4 (CLK), U604.62 (EECLK)
unnamed: R605.1, R609.1, U602.1 (DO)
unnamed: LS601.1, R616.1, R617.1
unnamed: R609.2, U602.3 (DI), U604.61 (EEDATA)
unnamed: C605.1, C607.1, LF602.2, U604.9 (VPLL)
unnamed: C604.1, C606.1, LF601.2, U604.4 (VPHY)
unnamed: R610.2, U604.14 (!RESET#)
unnamed: R611.2, U604.6 (REF)
unnamed: C611.1, U604.2 (OSCI), X601.1 (C1)
unnamed: C612.1, U604.3 (OSCO), X601.3 (C2)
unnamed: LED604.C, R614.2
unnamed: LED605.C, R615.2
unnamed: LED602.C, R612.2
unnamed: LED603.C, R613.2
unnamed: D602.3 (CH1), J601.3, U604.8 (DP)
unnamed: D602.4 (CH2), J601.2, U604.7 (DM)
unnamed: J604.5, R608.2
unnamed: J604.4, R607.2
unnamed: J604.3, R606.2
unnamed: J604.2, R602.2
unnamed: LED601.A, R601.2
RAM0_CEN: J602.4, U603.1 (/CE); also elsewhere on the board
RAM0_SCLK: J602.6, U603.6 (SCLK); also elsewhere on the board
RAM0_SIO0: J602.8, U603.5 (SI/SIO[0]); also elsewhere on the board
RAM0_SIO1: J602.2, U603.2 (SO/SIO[1]); also elsewhere on the board
RAM0_SIO2: U603.3 (SIO[2]); also elsewhere on the board
RAM0_SIO3: U603.7 (SIO[3]); also elsewhere on the board
RPI0_BUZZ: R617.2; also elsewhere on the board
RPI0_GPIO5: J603.14; also elsewhere on the board
RPI0_GPIO6: J603.12; also elsewhere on the board
RPI0_GPIO19: J603.10; also elsewhere on the board
RPI0_GPIO22: J603.16; also elsewhere on the board
RPI0_GPIO26: J603.8; also elsewhere on the board
RPI0_GPIO27: J603.18; also elsewhere on the board
RPIP_BUZZ: R616.2; also elsewhere on the board
RPIP_SCL1: J603.19; also elsewhere on the board
RPIP_SDA1: J603.20; also elsewhere on the board
TRG0: R608.1; also elsewhere on the board
TRG1: R607.1; also elsewhere on the board
TRG2: R606.1; also elsewhere on the board
TRG3: R602.1; also elsewhere on the board
UARTB_CTSN_TO_FTDI: U606.4 (INB); also elsewhere on the board
UARTB_FPGA_TO_FTDI: U606.3 (INA); also elsewhere on the board
UARTB_FTDI_TO_FPGA: U606.5 (OUTC); also elsewhere on the board
UARTB_RTSN_TO_FPGA: U606.6 (OUTD); also elsewhere on the board
UART_CTSN_TO_FTDI: U605.4 (INB); also elsewhere on the board
UART_FPGA_TO_FTDI: U605.3 (INA); also elsewhere on the board
UART_FTDI_TO_FPGA: U605.5 (OUTC); also elsewhere on the board
UART_RTSN_TO_FPGA: U605.6 (OUTD); also elsewhere on the board
V3P3: C608.1, C613.1, C614.1, C617.1, J603.22, J603.23, LF603.1, U603.8 (VDD), U605.1 (VCC1), U605.7 (EN1), U606.1 (VCC1), U606.7 (EN1); also elsewhere on the board
V3P3_R: C609.1, J604.6, LF603.2
V3P3_USB: C602.1, C603.1, C615.1, C616.1, C619.1, C620.1, C621.1, C622.1, C623.1, D602.6 (VP), LED602.A, LED603.A, LED604.A, LED605.A, LF601.1, LF602.1, R603.2, R604.2, R605.2, R610.1, R619.2, TP601.P$1, U601.1 (OUT), U602.6 (VCC), U604.20 (VCCIO), U604.31 (VCCIO), U604.42 (VCCIO), U604.50 (VREGIN), U604.56 (VCCIO), U605.10 (EN2), U605.16 (VCC2), U606.10 (EN2), U606.16 (VCC2)
V5P0_USB: C601.1, D601.1 (C), D601.2 (C), J601.1, U601.5 (/SHDN), U601.8 (IN)
V12: J603.26; also elsewhere on the board

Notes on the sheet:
Misc Circuits
Remote Trigger Receiver (QiaChip)
PSRAM with debug connector
Spare
To FPGA U301 page 3
To RPi 0 J101 page 1
FTDI USB Interface
USB Connector


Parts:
C701, C711, C715, C720, C724: 39p; 0402-CAP
C702, C703, C704, C706, C709, C710, C712, C713, C714, C716, C717, C719, C722, C723, C725, C726, C727, C728, C736, C737: 22u; 0805-CAP
C705, C707, C708, C731: 100u/25V; 2917-CAP
C718: 330u/25V; CAP-SMD-POL-8X10
C721, C732, C733, C735, C738, C740: 0.1u; 0402-CAP
C729: 10n; 0603-CAP
C730: 1n; 0603-CAP
C734, C739: DNP; 0402-CAP
D701, D702, D703, D704: DIODESOD128; SOD128
F701: 2920L600/16MR; 2920-FUSE
J701: M04X2_SHROUDED; M04X2-SHROUDED
J702: POWERJACK_PJ051AH; PJ051AH
LF701: FERRITE1206; 1206
Q701: MOSFET-NCHANNELSMD; SOT23-3
Q702: MOSFET-PCHANNEL_SO8; SO08
R702, R706, R710, R714, R718: 47k; 0402-RES
R703, R707, R711, R715, R721: 100k; 0402-RES
R704, R716, R720: 6.2k; 0402-RES
R705, R709, R717: 1k; 0402-RES
R708, R712: 8.66k; 0402-RES
R719: 15k; 0402-RES
R723: 0.01; 1206
R724: 10M; 0805
TP701, TP702, TP703, TP704, TP705, TP706: TESTPOINT_ROUND; TESTPAD_ROUND
U701, U704: MPM3650; QFN-24-MPS_FULL_CREAM
U702, U703, U705: RPL-30
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

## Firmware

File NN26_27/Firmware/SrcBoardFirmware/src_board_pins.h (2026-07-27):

// ---  NinjaNIRS 2024  ---
// Pin constants for NN22_VCCS_SrcAdapter02_s00 board
//
// Initial version: 2024-03-26
// Bernhard Zimmermann - bzim@bu.edu
// Boston University Neurophotonics Center
//

// Backplane pins: GPIO00 - GPIO06
const uint UART_TX_PIN = 0;
const uint UART_RX_PIN = 1;
const uint BOARD_SELECTN_PIN = 2;
//const uint STEP_PIN = 3; // defined in led_sel_fsm.pio
const uint LED_EN_IN_PIN = 4;
const uint STATUS_SELECT_PIN = 5;
const uint RESERVED_PIN = 6;

// Misc Pins
const uint LED_R_PIN = 8;
const uint LED_G_PIN = 7;
const uint SPARE_PINS[] = {19, 20};

// DAC pins
const uint CSN_DAC_PIN = 21;
const uint SCLK_DAC_PIN = 22;
const uint MOSI_DAC_PIN = 23;
const uint RESETN_DAC_PIN = 24;
const uint LDACN_DAC_PIN = 18;

// LED (Source optode) control pins
const uint VLED_EN_PIN = 10;
const uint LED_AD_PINS[] = {12, 13, 14, 15};
const uint LED_ENN_PIN = 16;
const uint DUMMY_EN_PIN = 17;
 
// Analog sense pins
const uint LED_CURR_SENSE_PIN = 26;
const uint LED_CURR_SENSE_ACH = 0;
const uint VIN_SENSE_PIN = 27;
const uint VIN_SENSE_ACH = 1;
const uint VNEG_SENSE_PIN = 28;
const uint VNEG_SENSE_ACH = 2;
const uint LED_COM_SENSE_PIN = 29;
const uint LED_COM_SENSE_ACH = 3;
const uint TEMP_SENSE_ACH = 4;

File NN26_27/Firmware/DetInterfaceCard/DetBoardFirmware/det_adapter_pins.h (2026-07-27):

// ---  NinjaNIRS 2022  ---
// Pin constants for NN22_RPi_DetAdapter00_s02_R66R67 board
//
// Initial version: 2022-12-12
// Bernhard Zimmermann - bzim@bu.edu
// Boston University Neurophotonics Center
//


// Backplane pins: GPIO00 - GPIO06
const uint UART_TX_PIN = 0;
const uint UART_RX_PIN = 1;
const uint BOARD_SELECT_PIN = 2;
//const uint TRG_PIN = 3; // check also adcacq.pio
const uint END_CYC_PIN = 4;
const uint STATUS_SELECT_PIN = 5;
const uint RESERVED_PIN = 6;

// Misc Pins
const uint A_COMM_PIN = 7;
const uint OPT_EN_VP_PIN = 8;
const uint OPT_EN_VN_PIN = 9;
const uint LED_R_PIN = 10;
const uint LED_G_PIN = 11;

// ADC pins
// 4 ADCs with dual-data SPI interface
const uint CSN_A3_PIN = 12;
const uint SCLK_A3_PIN = 13;
const uint MOSI_A3_PIN = 14;
const uint MISO_A3_PIN = 15;
 
const uint CSN_A1_PIN = 16;
const uint SCLK_A1_PIN = 17;
const uint MOSI_A1_PIN = 18;
//const uint MISOB_A1_PIN = 19; // only using one MISO wire
const uint MISO_A1_PIN = 20;

const uint CSN_A4_PIN = 21;
const uint SCLK_A4_PIN = 22;
const uint MOSI_A4_PIN = 23;
const uint MISO_A4_PIN = 24;

const uint CSN_A2_PIN = 25;
const uint SCLK_A2_PIN = 26;
const uint MOSI_A2_PIN = 27;
//const uint MISOB_A2_PIN = 28; // only using one MISO wire
const uint MISO_A2_PIN = 29;

// Map adc results to detectors
const uint DET_ADC_MAP[] = {0, 1, 5, 4, 2, 3, 7, 6};

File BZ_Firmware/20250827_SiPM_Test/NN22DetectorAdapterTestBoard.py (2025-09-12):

# ---  NinjaNIRS 2022  ---
# Helper module for NN22_RPi_DetAdapter00_TestBoard00
#
# Initial version: 2022-12-19
# Bernhard Zimmermann - bzim@bu.edu
# Boston University Neurophotonics Center
#

import board
import digitalio
import time
import pwmio
import busio
from analogio import AnalogIn

class TestBoard:
    def __init__(self):
        # Init GPIO
        self.ledR = digitalio.DigitalInOut(board.GP13)
        self.ledG = digitalio.DigitalInOut(board.GP14)
        self.ledR.direction = digitalio.Direction.OUTPUT
        self.ledG.direction = digitalio.Direction.OUTPUT

        self.targetRun = digitalio.DigitalInOut(board.GP12) # on target: RP2040 'run' pin
        self.targetBoardSelect = digitalio.DigitalInOut(board.GP7) # on target: GPIO02
        self.targetTrig = digitalio.DigitalInOut(board.GP8) # on target: GPIO03
        self.targetEndCyc = digitalio.DigitalInOut(board.GP9) # on target: GPIO04
        self.targetStatusSelect = digitalio.DigitalInOut(board.GP10) # on target: GPIO05
        #targetReservedPin = board.GP11 # on target: GPIO06

        self.targetRun.direction = digitalio.Direction.OUTPUT
        self.targetBoardSelect.direction = digitalio.Direction.OUTPUT
        self.targetBoardSelect.value = 1
        self.targetTrig.direction = digitalio.Direction.OUTPUT
        self.targetEndCyc.direction = digitalio.Direction.OUTPUT
        self.targetStatusSelect.direction = digitalio.Direction.OUTPUT

        self.buzz = pwmio.PWMOut(board.GP22, duty_cycle=0, frequency=1000, variable_frequency=True)
        #self.buzz.duty_cycle = 2**15
        self.button = digitalio.DigitalInOut(board.GP15)

        self.dac = Bh2226f()
        self.dac.setCHvalR0(0,0)

        self.nSamples = 10
        self.adcCalConst = -6.25e-4/self.nSamples # convert ADC value to voltage

        self.uart = busio.UART(board.GP4, board.GP5, baudrate=6000000)

        self.analogVN20 = AnalogIn(board.A0)
        self.analogV6P5 = AnalogIn(board.A1)
        self.analogV3P3 = AnalogIn(board.A2)

        self.resetTargetBoard()

    def getSupplyRails(self):
        # This function reads the voltages of three supply rails on
        # the target detector adapter card.
        reslist = []
        val = self.analogV6P5.value * 3.3 / 65535 # voltage at the RP2040 pin
        val = val * (3.3+5.6)/3.3 # voltage at rail, considering voltage divider
        reslist.append(val)
        val = self.analogV3P3.value * 3.3 / 65535 # voltage at the RP2040 pin
        val = val * (3.3+3.3)/3.3 # voltage at rail, considering voltage divider
        reslist.append(val)
        val = self.analogVN20.value * 3.3 / 65535 # voltage at the RP2040 pin
        val = val - 33/3.3*(3.3-val) # voltage at rail, considering voltage divider
        reslist.append(val)
        return reslist

    def getOneTargetSample(self):
        # This function collects one sample of all 8 ADC channels of the
        # connected target detector adapter card.
        self.uart.reset_input_buffer()
        for isample in range(0,self.nSamples+1): # first sample will be discarded by target
            self.targetTrig.value = 1
            self.targetTrig.value = 0
        self.targetEndCyc.value = 1
        self.targetEndCyc.value = 0

        self.targetBoardSelect.value = 0
        buf = self.uart.read(28)
        self.targetBoardSelect.value = 1

        if buf is None:
            print("No data received from target.")
            return []
        elif len(buf)<28:
            print("Not enough data received from target.")
            return []

        # check packet header bytes
        if not(buf[0]==253 and buf[1]==252):
            print("Bad header received from target.")

        # check sample counter
        if buf[2]!=self.sampleCount:
            print("Bad sample count received from target.")
        self.sampleCount = (buf[2]+1)%256

        # convert received payload bytes to results list
        # N_BYTES_PER_DET = 3
        reslist = []
        for ich in range(0, 8):
            val = buf[3+ich*3] + buf[3+ich*3+1]*256 + buf[3+ich*3+2]*65536
            # correct for two's complement and invert result
            if val>8388607: # equivalent: val>((2**23)-1)
                val = 16777216-val # equivalent: 2**24-val
            else:
                val = -val
            reslist.append(val)

        # check packet trailer byte
        if buf[27]!=0:
            print("Bad trailer received from target.")

        return reslist

    def getTargetStatus(self):
        # This fuction collects one status packet of the
        # connected target detector adapter card.
        self.uart.reset_input_buffer()
        self.targetStatusSelect.value = 1
        self.targetEndCyc.value = 1
        self.targetEndCyc.value = 0
        self.targetStatusSelect.value = 0

        self.targetBoardSelect.value = 0
        buf = self.uart.read(18)
        self.targetBoardSelect.value = 1

        if buf is None:
            print("No data received from target.")
            return []
        elif len(buf)<18:
            print("Not enough data received from target.")
            return []

        # check packet header bytes
        if not(buf[0]==239 and buf[1]==238):
            print("Bad status packet header received from target.")

        # check sample counter
        if buf[2]!=self.sampleCount:
            print("Bad sample count received from target.")
        self.sampleCount = (buf[2]+1)%256

        # convert received payload bytes to results list
        reslist = []
        #reslist.append(buf[3:11].hex()) # unique ID # does not work in this Python version
        reslist.append(''.join('{1:02x}'.format(*d) for d in enumerate(buf[3:11])))
        reslist.append('v{:d}.{:d}'.format(buf[11], buf[12])) # firmware version
        temp = 27.0 - ((buf[13] + buf[14]*(1<<8)) * 3.3/(1<<12) - 0.706)/0.001721
        reslist.append('{:4.1f}C'.format(temp))

        # check packet trailer byte
        if buf[17]!=0:
            print("Bad status packet trailer received from target.")

        return reslist

    def resetTargetBoard(self):
        self.targetRun.value = 0
        time.sleep(0.01)
        self.targetRun.value = 1
        time.sleep(1.5)
        self.sampleCount = 0

class Bh2226f:
    # class for ROHM BH2226F 8 bit 8 channel D/A Converter
    # only functionality required for this project implemented
    def __init__(self):
        # set on-board Vreg to PWM mode to reduce ripple
        self.pwmmode = digitalio.DigitalInOut(board.GP23)
        self.pwmmode.direction = digitalio.Direction.OUTPUT
        self.pwmmode.value = True

        # pin definitions for serial interface
        self.resetn = digitalio.DigitalInOut(board.GP20)
        self.resetn.direction = digitalio.Direction.OUTPUT
        self.resetn.value = False
        self.clk = digitalio.DigitalInOut(board.GP18)
        self.clk.direction = digitalio.Direction.OUTPUT
        self.clk.value = False
        self.csn = digitalio.DigitalInOut(board.GP17)
        self.csn.direction = digitalio.Direction.OUTPUT
        self.csn.value = True
        self.so = digitalio.DigitalInOut(board.GP16) # "MISO"
        self.di = digitalio.DigitalInOut(board.GP19) # "MOSI"
        self.di.direction = digitalio.Direction.OUTPUT
        self.di.value = False

        # start up DAC
        self.resetn.value = True # release reset
        time.sleep(0.001)
        self.powerDownRelease()
        self.selectDA() # set outputs to analog mode

    def sendInstruction(self, addr, val): # send a single instruction
        data = (addr<<8) + val
        self.csn.value = False
        for ibit in range(11, -1, -1):
            self.di.value = (data >> ibit) &1
            self.clk.value = False
            self.clk.value = True
        self.csn.value = True
        self.clk.value = False
        self.di.value = False

    def setCHval(self, ch, val): # ch in range [0..7], val in range [0..255]
        addrlist = [0b1000, 0b0100, 0b1100, 0b0010, 0b1010, 0b0110, 0b1110, 0b0001]
        self.sendInstruction(addrlist[ch], val)

    def setCHvalR0(self, ch, val): # set all others to 0
        for nch in range(0, 8):
            if nch == ch:
                nval = val
            else:
                nval = 0
            self.setCHval(nch, nval)

    def powerDownRelease(self): # init command required by dac
        self.sendInstruction(0b1001, 0)

    def selectDA(self): # set all outputs to analog mode
        self.sendInstruction(0b0011, 0b11111111)

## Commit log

2025-05-07 starting on bias voltage trim circuit
    [pot-calcs.ods, vreg-dac-lt3014.kicad_pcb, vreg-dac-lt3014.kicad_sch]
2025-05-08 working on sch
    [vreg-dac-lt3014.kicad_sch]
2025-05-08 working on layout
    [vreg-dac-lt3014.kicad_pcb, vreg-dac-lt3014.kicad_sch]
2025-05-09 new placement
    [vreg-dac-lt3014.kicad_pcb, vreg-dac-lt3014.kicad_sch]
2025-05-09 candidate V1.0 LT3014 board
    [lt3014-test-B_Cu.gbr, lt3014-test-B_Mask.gbr, lt3014-test-B_Paste.gbr, lt3014-test-B_Silkscreen.gbr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]
2025-05-12 small tweaks before V1.0 fab
    [lt3014-test-B_Cu.gbr, lt3014-test-B_Mask.gbr, lt3014-test-B_Silkscreen.gbr, lt3014-test-Edge_Cuts.gbr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]
2025-06-04 readme, schematic notes
    [lt3014-test.kicad_sch]
2025-06-26 starting schem for HV/splitter for SiPM
    [boost.kicad_sch, sipm-hv-splitter.kicad_pcb, sipm-hv-splitter.kicad_sch, tia.kicad_sch]
2025-06-30 working on SiPM power supply schem
    [boost.kicad_sch, sipm-hv-splitter.kicad_pcb, sipm-hv-splitter.kicad_sch, tia.kicad_sch]
2025-06-30 starting placement
    [boost.kicad_sch, sipm-hv-splitter.kicad_pcb, sipm-hv-splitter.kicad_sch]
2025-06-30 random placement for area estimate
    [sipm-hv-splitter.kicad_pcb, sipm-hv-splitter.kicad_sch]
2025-06-30 add ISP
    [boost.kicad_sch, sipm-hv-splitter.kicad_pcb, sipm-hv-splitter.kicad_sch]
2025-06-30 fix some MCU pins
    [sipm-hv-splitter.kicad_sch]
2025-07-01 working on 2.5 in placement
    [boost.kicad_sch, sipm-hv-splitter.kicad_pcb, sipm-hv-splitter.kicad_sch]
2025-07-01 routing madness
    [boost.kicad_sch, sipm-hv-splitter.kicad_pcb, sipm-hv-splitter.kicad_sch, tia.kicad_sch]
2025-07-02 working on bias filter changes
    [boost.kicad_sch, sipm-hv-splitter.kicad_pcb, sipm-hv-splitter.kicad_sch, tia.kicad_sch]
2025-07-03 routing almost done
    [sipm-hv-splitter.kicad_pcb]
2025-07-03 routing complete
    [boost.kicad_sch, sipm-hv-splitter.kicad_pcb, sipm-hv-splitter.kicad_sch]
2025-07-03 draft schematic PDF and Gerbers
    [sipm-hv-splitter-B_Cu.gbr, sipm-hv-splitter-B_Mask.gbr, sipm-hv-splitter-B_Silkscreen.gbr, sipm-hv-splitter-Edge_Cuts.gbr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]
2025-07-03 working on BOM
    [boost.kicad_sch, sipm-hv-splitter.kicad_sch, tia.kicad_sch]
2025-07-03 finish BOM entries on schematic
    [boost.kicad_sch, sipm-hv-splitter.csv, sipm-hv-splitter.kicad_sch, tia.kicad_sch]
2025-07-07 working on layout updates
    [sipm-hv-splitter.kicad_pcb, sipm-hv-splitter.kicad_sch]
2025-07-07 Candidate V1.0 for review/fab
    [boost.kicad_sch, sipm-hv-splitter-B_Cu.gbr, sipm-hv-splitter-B_Mask.gbr, sipm-hv-splitter-B_Silkscreen.gbr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]
2025-07-08 Update gerber zip
    [sipm-hv-splitter-B_Cu.gbr, sipm-hv-splitter-B_Mask.gbr, sipm-hv-splitter-B_Silkscreen.gbr, sipm-hv-splitter-Edge_Cuts.gbr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]
2025-07-09 add mtg holes, L2 gnd fill
    [boost.kicad_sch, sipm-hv-splitter-B_Cu.gbr, sipm-hv-splitter-B_Mask.gbr, sipm-hv-splitter-B_Silkscreen.gbr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]
2025-07-10 finished V1.0 hv/splitter?
    [sipm-hv-splitter-BOM.csv, sipm-hv-splitter-BOM.ods, sipm-hv-splitter.csv]
2025-07-10 update to V1.0b, change min hole to 0.2mm
    [sipm-hv-splitter-B_Cu.gbr, sipm-hv-splitter-B_Mask.gbr, sipm-hv-splitter-B_Silkscreen.gbr, sipm-hv-splitter-Edge_Cuts.gbr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]
2025-08-27 add temperature readout
    [sipm-hv-splitter.kicad_sch]
2025-09-03 update software, add dark box
    [arc.scad, box.scad, box.stl]
2025-09-10 dark box for testing
    [box.scad, box.stl, lid.stl]
2025-09-10 tweak box
    [box.scad, box.stl]
2025-09-12 new operating firmware, some doco
    [NN22_RPi_DetAdapter02_s00.drills.xln]
2026-02-03 update testing
    [boost.kicad_sch, box.scad, crimps.stl, crimps2.stl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]
2026-02-12 more testing
    [load_reg.kicad_pcb, load_reg.kicad_sch]
2026-03-03 Update README and tweak voltage / ADC numbers

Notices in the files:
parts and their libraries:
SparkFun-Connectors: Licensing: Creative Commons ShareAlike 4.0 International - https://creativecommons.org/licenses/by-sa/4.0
